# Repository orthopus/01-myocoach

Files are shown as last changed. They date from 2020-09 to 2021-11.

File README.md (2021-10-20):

# 01-myocoach





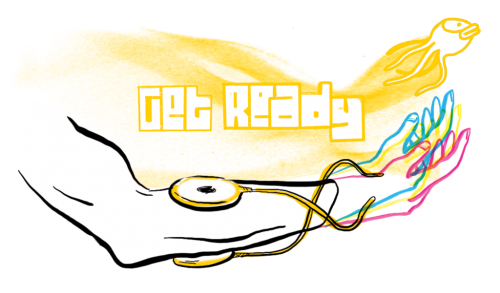
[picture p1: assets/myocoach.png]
myocoach


---

The **MyoCoach** is a device for upper limb amputees who wish to wear a myoelectric prosthesis. It allows you to practice the contraction of the forearm muscles thanks to a video game inspired by Flappy Bird, and to train the control of the future prosthesis.

The MyoCoach can also be used by health professionals, particularly prosthetist (CPO) and occupational therapists, as it allows the myoelectric sensors to be placed correctly and adjusted for optimal use of myoelectric prostheses.

The MyoCoach makes it possible to :

* Measure muscle potential with the help of myoelectric sensors
* Define the optimal sensor position
* Adjusting the sensors using potentiometers
* Exercise in muscle contraction and coordination

The **MyoCoach** is made up of different elements :

* 2 EMG sensors to read the patient's myoelectric signals (EMG)
* 1 box to transfer data to the computer with an Arduino Board
* A holder to hold the sensors on the patient's arm
* A PC to run the UI application for EMG data visualization

> :warning: Today, the MyoCoach uses sensors from the brand Ottobock (Ref 13E202). One day, ORTHOPUS will propose one, but not at the price of 1000€ !
> 

## Warning notice before starting

The versions of our solutions reproduced in Do It Yourself do not have the CE marking. It can only be apply to solutions developed and sold by ORTHOPUS which follow the regulations in force.
ORTHOPUS cannot guarantee the “quality” of solutions replicated by third parties thanks to documentation shared on github.

## D.I.Y Level

:star: :star:

**Required devices** : to make your own Myo coach, we will need a 3D printer and some basics electronics tools like a soldering iron + soldering accessories (you will find a detailed list of equipment in the [user manual](./docs/user-manual.md).

## How to make your own

We give more details about how to get the best experiences with the **Myo Coach** in the [user manual](./docs/user-manual.md).

You can design the MyoCoach for less than **30€**. More details in the [COSTS](COSTS.md) file.

Follow this steps to make your own **Myo Coach**

**:one: Download the src**

Download the [latest release](https://github.com/orthopus/01-myocoach/releases/latest)

or clone the **01-myocoach** repository

```bash
$ git clone https://github.com/orthopus/0102-myocoach-diy.git
```

**:two: Make the box**

Follow the [manufacturing manual](./docs/manufacturing-manual.md)

**:three: Flash the Arduino Board**

Follow the [firmware programming manual](./docs/firmware-programming-manual.md)

**:four: Install the Application server on a Raspberry Pi board**

Follow the [App server programming manual](./docs/server-programming-manual.md)

## Contribution
Your contribution to the MyoCoach project is welcome!

* Have you discovered a bug or you have an improvement ideas ?
  * Go to the GitHub [issues](https://github.com/orthopus/01-myocoach/issues) of the project.
* You have time, some Maker skills and you want to help us ?
  * Read the [CONTRIBUTING](CONTRIBUTING.md) file to help us to go to the **Myo Coach v2.0**
  * Read the [CODEOFCONDUCT](CODEOFCONDUCT.md) file to know community standards

## Contact

If you wish to contact us, you can send a message to contact@orthopus.com

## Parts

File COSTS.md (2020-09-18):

# 0113-MyoCoach-DIY :<br>Price Transparency

## Raw Material Price
| Description | Quantity | Unit Price | Price |
| --- | --- | --- | --- |
| Sensor Support (3D print)| 2 | 0.60€ | 1.20€ |
| Box Casing (3D print)| 1 | 2.18€ | 2.18€ |
| Arduino Board Uno | 1 | 20.00€ | 20.00€ |
| female pin header strip | 1 | 1.17€ | 1.17€ |
| male pin header strip | 1 | 1.07€ | 1.07€ |
| Self-tapping screws | 8 | 0.02€ | 0.16€ |
| strap with velcro and buckle | 1 | 0.50€ | 0.50€ |
| set of electronic cables | 1 | 2.68€ | 2.68 € |
| | | **Total**      | **28.96€** |

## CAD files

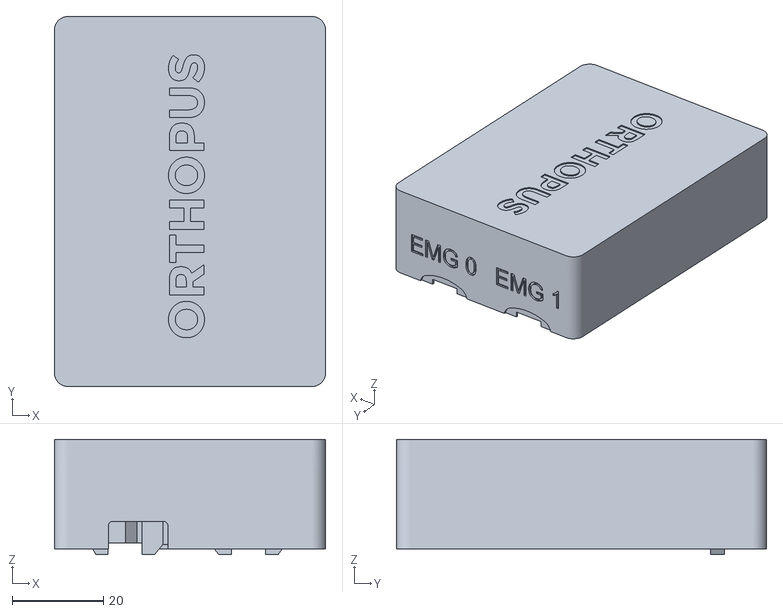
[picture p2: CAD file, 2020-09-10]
src/hardware/casing/Casing Up.stl
59.3 x 80.9 x 25.2

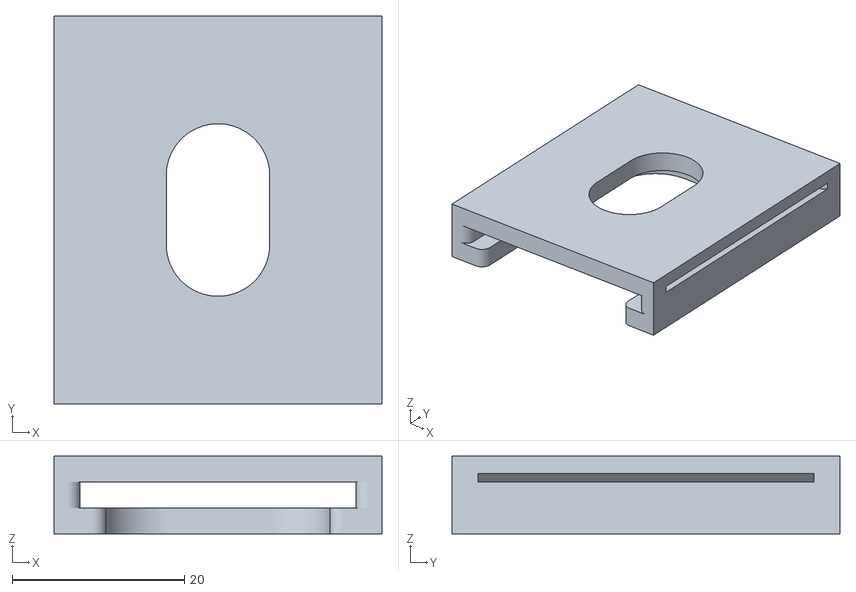
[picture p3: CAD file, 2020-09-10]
src/hardware/casing/Sensor Support 13E202.stl
38.0 x 45.0 x 9.00

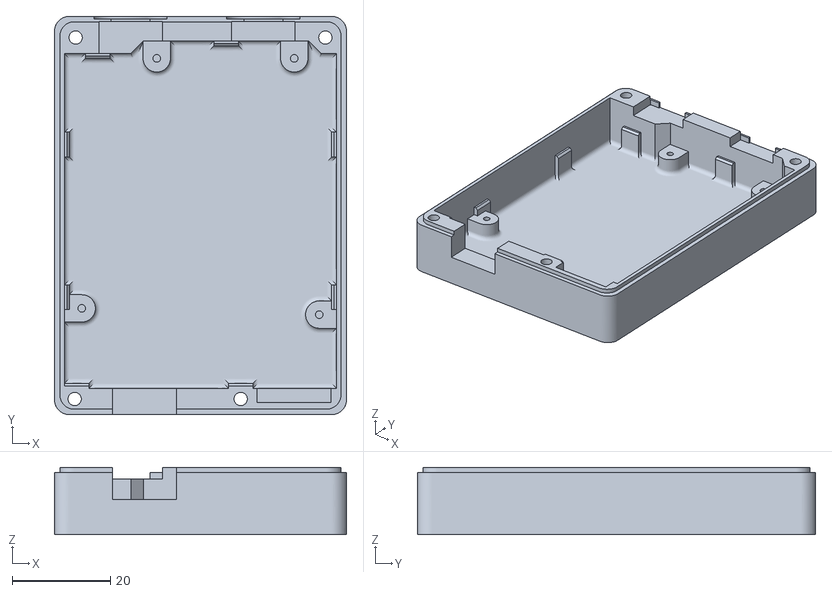
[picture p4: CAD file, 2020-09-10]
src/hardware/casing/Casing Down.stl
59.3 x 80.9 x 13.7

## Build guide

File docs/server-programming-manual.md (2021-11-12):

# 0113-MyoCoach-DIY :<br>Server Programming Guide

myocoach

---

The MyoCoach v2.0 application allows the visualization of raw EMG signals and allows users to train by doing exercises or through video games. As it is a web application with a responsive design, it can be accessed using a web browser installed on a desktop workstation or on a mobile device such as a smartphone or a tablet.  

The MyoCoach v2.0 application has been created using the following technologies :
* Back-end development : Python Flask, SQLite, Socket-IO
* Front-end development : TypeScript, React, Material-UI
* Games development : Godot Engine

The original environment board chosen to host the application is a Raspberry Pi 3 model B+ but the installation process remains identical with later versions of Raspberry Pi boards and can probably be adapted for other development boards or desktop workstations running under a GNU/Linux OS.

## OS setup

Download a Raspberry Pi OS Lite image available at the following address from a workstation : https://www.raspberrypi.org/software/operating-systems/#raspberry-pi-os-32-bit

Unzip the downloaded archive to get the image file (.img file extension).

From a terminal, go to the directory where the .img file is then connect a MicroSD card on the workstation (16Gb A1 minimum recommended). The MicroSD card has to be unmounted if it has been mounted automatically.

Then run the following command :

Note : Replace _2021-05-07-raspios-buster-armhf-lite_ by the actual .img file name.

```bash
~> sudo dd bs=1m if=2021-05-07-raspios-buster-armhf-lite.img of=/dev/rdisk2
```

Eject the MicroSD card from the workstation SD slot then insert it in the Raspberry Pi MicroSD slot. Connect a screen, a keyboard and an ethernet cable then power on the Raspberry Pi board. Wait for the system to be ready.

Once the system started, authenticate on the terminal with "pi" user (password: raspberry).

## SSH access

On the Raspberry Pi, enable ssh access allow remote connection from other workstation. Run the following command :

```bash
pi@raspberrypi:~ $ sudo raspi-config
```

Select the following option on the user interface : _3 Interface Options_, _P2 SSH_ then select _Yes_. Finally, select _Finish_ to save configuration and get back to the command prompt.

## Keyboard layout

It may be necessary to configure the type of keyboard used. Run the following command :

```bash
pi@raspberrypi:~ $ sudo raspi-config
```

Select the following option on the user interface : _5 Localisation Options_, _L3 Keyboard_ then follow the instructions to configure the keyboard (for example : Logitech, French-French (legacy, alt.), The default for the keyboard layout, No compose key). Finally, select _Finish_ to save configuration and back to the command prompt.

## Pi password

To change the default password, run the following command :

```bash
pi@raspberrypi:~ $ passwd
```

Then type the current password, the new password and finally confirm.

## Installing system packages

To install software from the Internet it is necessary to wire-up the Raspberry Pi to a router using the Ethernet interface. To do so plug an RJ45 cable on the Ethernet port of the board and connect-it to a router that has a connection to the Internet.

Before installing new components, it may be necessary to get the up-to-date packages list :

```bash
pi@raspberrypi:~ $ sudo apt udpate
```

As well as the packages installed by default :

```bash
pi@raspberrypi:~ $ sudo apt upgrade
```

The MyoCoach setup needs several packages to work properly : Pip3, VirtualEnv, Flask, NodeJs, SQLite.

First add nodesource apt repository in order to be able to get the nodejs packages :

```bash
pi@raspberrypi:~ $ curl -sL https://deb.nodesource.com/setup_16.x | sudo bash -
```

Then install the packages :

```bash
pi@raspberrypi:~ $ sudo apt install nodejs git python3-pip python3-flask sqlite3 virtualenv
```

## Application setup

### Get the application code

To get the latest version of the application source code, keep the board connected to the Internet using the Ethernet port and run the following commands :

```bash
pi@raspberrypi:~ $ git clone https://github.com/orthopus/01-myocoach.git
```

### Fetch application dependencies

On the Raspberry Pi, go to the MyoCoach webapp directory :

```bash
pi@raspberrypi:~ $ cd 01-myocoach/src/software/webapp/
```

To get the Python packages, run the following command :

```bash
pi@raspberrypi:~/01-myocoach/src/software/webapp $ sudo pip3 install -r requirements.txt
```

Run the following command to get the nodejs dependencies :

```bash
pi@raspberrypi:~/01-myocoach/src/software/webapp $ npm install
```

### Environment variables and compilation

Create a copy of the _.env.example_ file named _.env_ :

```bash
pi@raspberrypi:~/01-myocoach/src/software/webapp $ cp .env.example .env
```

Then check its content and adapt it if necessary using a text editor :

```bash
pi@raspberrypi:~/01-myocoach/src/software/webapp $ nano .env
```

.env
```bash
NODE_ENV=production
ENDPOINT=http://app.myocoach.lan
```

The run the Webpack compilation with the following command :

```bash
pi@raspberrypi:~/01-myocoach/src/software/webapp $ npx webpack --config webpack.prod.js
```

## Networking

### Hostname

In objective to change the MyoCoach hostname (currently raspberrypi), open the system settings interface with the following commands :

```bash
pi@raspberrypi:~ $ sudo raspi-config
```

On the system settings interface, select _1 System Options_, _S4 Hostname_ then _OK_. Type the new name _"myocoach"_. Select _Finish_ to save the configuration. Finally, select _Yes_ to reboot the system for the changes take effect.

The hostname of the _hosts_ file has to be refreshed to save the new hostname.

```bash
pi@myocoach:~ $ less /etc/hosts
```

hosts
```bash
127.0.0.1       localhost
::1             localhost ip6-localhost ip6-loopback
ff02::1         ip6-allnodes
ff02::2         ip6-allrouters

127.0.1.1       myocoach
```

### Avahi configuration

Open the avahi configuration file in order to make MyoCoach get the _"myocoach.lan"_ name on the network :

```bash
pi@myocoach:~ $ sudo nano /etc/avahi/avahi-daemon.conf
```

avahi-daemon.conf
```bash
...
[server]
host-name=myocoach
domain-name=lan
...
```

Restart the service for the changes to take effect with the following commands :

```bash
pi@myocoach:~ $ sudo systemctl reload avahi-daemon
pi@myocoach:~ $ sudo systemctl restart avahi-daemon
```

### Access Point - RaspAP

To enable wireless on the Raspberry Pi use the following command :

```bash
pi@myocoach:~ $ sudo rfkill unblock wlan
```

```bash
pi@myocoach:~ $ curl -sL https://install.raspap.com | bash
```

Then follow the instructions.

Once the Raspberry Pi rebooted, connect to the network raspap-webui (psk: ChangeMe) with the workstation. Go to the access point management interface from the workstation with a web browser at the following address _10.3.141.1_. Authenticate to the interface with the "admin" username (password: secret) then go to the Authentication section to change the password.

### Captive portal

The captive portal is managed by the Nodogsplash application.

```bash
pi@myocoach:~ $ sudo apt-get install libmicrohttpd-dev
```

```bash
pi@myocoach:~ $ sudo mkdir /srv/nodogsplash
pi@myocoach:~ $ sudo chown pi /srv/nodogsplash
pi@myocoach:~ $ sudo chgrp pi /srv/nodogsplash
pi@myocoach:~ $ git clone https://github.com/nodogsplash/nodogsplash.git /srv/nodogsplash
```

To compile Nodogsplash, run the following commands :

```bash
pi@myocoach:~ $ cd /srv/nodogsplash
pi@myocoach:~ $ make
pi@myocoach:~ $ sudo make install
```

Open the configuration file nodogsplash.conf :

```bash
pi@myocoach:~ $ sudo nano /etc/nodogsplash/nodogsplash.conf
```

Change the following lines :

```bash
GatewayInterface wlan0
GatewayAddress 10.3.141.1
RedirectURL http://10.3.141.1:2050/redirect.html
```

In the FirewallRuleSet users-to-router object, add the following line :

```bash
FirewallRule allow tcp port 5000
```

Save and close the file.

Remove nodogsplash default captive portal html files :

```bash
pi@myocoach:~ $ sudo rm -rf /etc/nodogsplash/htdocs
```

Then create a link to myocoach captive portal html files :

```bash
pi@myocoach:~ $ sudo ln -s /home/pi/01-myocoach/src/software/captiveportal /etc/nodogsplash/htdocs
```

Open the configuration file dnsmasq.conf :

```bash
pi@myocoach:~ $ sudo nano /etc/dnsmasq.conf
```

Add or change the following line :

```bash
address=/#/10.3.141.1
```

Save and close the file. 

Copy the nodogsplash.service file then enable start at boot :

```bash
pi@myocoach:~ $ sudo cp /srv/nodogsplash/debian/nodogsplash.service /lib/systemd/system/
pi@myocoach:~ $ sudo systemctl enable nodogsplash.service
```

Enable start at boot :

```bash
pi@myocoach:~ $ sudo systemctl enable dnsmasq.service
```

Finally, reboot the system to save the changes.

### Lighttpd configuration

In objective to access the MyoCoach web interface and the RaspAP web interface as well, Lighttpd has to be configured.

First, the RaspAP web interface must have restricted access to the _raspap.myocoach.lan_ subdomain name.

```bash
pi@myocoach:~ $ sudo nano /etc/lighttpd/conf-available/50-raspap-router.conf
```

50-raspap-router.conf
```bash
server.modules += ("mod_rewrite")

$HTTP["host"] == "raspap.myocoach.lan" {
  $HTTP["url"] =~ "^/(?!(dist|app|ajax|config)).*" {
    url.rewrite-once = ( "^/(.*?)(\?.+)?$"=>"/index.php/$1$2" )
    server.error-handler-404 = "/index.php"
  }
}
```

Next, create a new file to declare the virtual host _app.myocoach.lan_.

```bash
pi@myocoach:~ $ sudo nano /etc/lighttpd/conf-available/40-myocoach.conf
```

40-myocoach.conf
```bash
server.modules += ( "mod_proxy" )

# proxy myocoach
$HTTP["host"] == "app.myocoach.lan" {
  proxy.debug = 1
  proxy.server = ( "" => ( ( "host" => "10.3.141.1", "port" => "5000" ) ) )
  proxy.header = ( "upgrade" => "enabled" )
}
```

Then, create a link to activate this new host.

```bash
pi@myocoach:~ $ cd /etc/lighttpd/conf-enabled/
pi@myocoach:~ $ sudo ln -s ../conf-available/40-myocoach.conf
```

At last, reboot the service for the changes to take effect.

```bash
pi@myocoach:~ $ sudo systemctl reload lighttpd
pi@myocoach:~ $ sudo systemctl restart lighttpd
```

## MyoCoach service

Create a link named myocoach in the /srv directory to the webapp directory :

```bash
pi@myocoach:~ $ sudo ln -s /home/pi/01-myocoach/src/software/webapp /srv/myocoach
```

Create a link named ledbutton in the /srv directory to the ledbutton directory :

```bash
pi@myocoach:~ $ sudo ln -s /home/pi/01-myocoach/src/software/ledbutton /srv/ledbutton
```

Create the MyoCoach systemd service :

```bash
pi@myocoach:~ $ cd /lib/systemd/system
pi@myocoach:/lib/systemd/system $ sudo nano myocoach.service
```

myocoach.service
```bash
[Unit]
Description= Controls myocoach webapp service
Requires= lighttpd.service
After= lighttpd.service

[Install]
WantedBy= multi-user.target

[Service]
Type= simple
User= root
WorkingDirectory= /srv/myocoach/app
ExecStart= /bin/python3 ./app.py
ExecStartPost= /bin/bash /srv/ledbutton/set_led_color.sh 0 0 255 0
ExecStop= /bin/kill -2 $MAINPID
ExecStopPost= /bin/bash /srv/ledbutton/set_led_color.sh 255 255 255 0
```

To start the service run the following command :

```bash
pi@myocoah:~ $ sudo systemctl start myocoach.service
```

To enable the service at system boot run the following command :

```bash
pi@myocoah:~ $ sudo systemctl enable myocoach.service
```

The MyoCoach web interface is now reachable at the following address :
_http://app.myocoach.lan_

And the RaspAP web interface is now reachable at the following address :
_http://raspap.myocoach.lan_

## LED Power Button Configuration (optional)

Optionally the MyoCoach can be equipped with a LED Power Button. It allows users to have information about the system state and proceed to a more graceful Power-OFF of the board (ie. cleaner than unplugging the power cable).

Create systemd services :

```bash
pi@myocoach:~ $ cd /lib/systemd/system
pi@myocoach:/lib/systemd/system $ sudo nano enlight_led.service
```

enlight_led.service
```bash
[Unit]
Description= Launch enlight_led.service

[Install]
WantedBy=multi-user.target

[Service]
Type= simple
User= pi
WorkingDirectory= /srv/ledbutton
ExecStart= /bin/bash ./enlight_led.sh
```

```bash
pi@myocoach:/lib/systemd/system $ sudo nano check_color_changed.service
```

check_color_changed.service
```bash
[Unit]
Description= Restarts enlight_led.service
Requires=basic.target
After=basic.target

[Install]
WantedBy=multi-user.target

[Service]
Type= oneshot
ExecStart= /usr/bin/systemctl restart enlight_led.service
```

```bash
pi@myocoach:/lib/systemd/system $ sudo nano check_color_changed.path
```

check_color_changed.path
```bash
[Unit]
Wants= check_color_changed.service

[Path]
PathChanged= /srv/ledbutton/led_color.txt

[Install]
WantedBy=basic.target
```

```bash
pi@myocoach:/lib/systemd/system $ sudo nano set_led_color_on_system_startup.service
```

set_led_color_on_system_startup.service
```bash
[Unit]
Description= Set led color on system startup
Requires= basic.target
After=basic.target

[Install]
WantedBy=multi-user.target

[Service]
Type= oneshot
WorkingDirectory= /srv/ledbutton
ExecStart= /bin/bash ./set_led_color.sh 255 255 255 0
```

Enable start at boot :

```bash
pi@myocoach:~ $ sudo systemctl enable enlight_led.service
pi@myocoach:~ $ sudo systemctl enable check_color_changed.service
pi@myocoach:~ $ sudo systemctl enable check_color_changed.path
pi@myocoach:~ $ sudo systemctl enable set_led_color_on_system_startup.service
```

Open the configuration file config.txt :

```bash
pi@myocoach:~ $ sudo nano /boot/config.txt
```

Add the following line :

```bash
dtoverlay=gpio-shutdown
```

Save and close the file. Finally, reboot the system to apply the changes.
```bash
pi@myocoach:~ $ sudo reboot
```

## Add new Games

The MyoCoach application has been designed to host video games developed using the Godot environment and that are adapted to use EMG signals as inputs.

Further information about game development with Godot can be found on Godot Engine website : _https://godotengine.org/_

To integrate new games in the MyoCoach environment and make them available from the web application, here are some guide-lines :

As there are only two EMG signals, and thus two possible inputs, the gameplay has to be kept simple. These EMG signals are mapped to InputEventMouseMotion in order to keep the "analog" values of signals. Depending on the game design, the value of EMG signals can be used as proportional inputs directly or to trigger events when they exceed a defined threshold.

A folder has to be created under the public/games/ directory for each hosted game. As an exemple to add "Squash" game, run the following command :

```bash
pi@myocoach:~ $ cd /srv/myocoach/public/games/ 
pi@myocoach:/srv/myocoach/public/games $ mkdir squash
```

From the Godot development environment, the games must be exported using an HTML5 template. Once exported, if the name of the export chosen is _game.html_, then get the files _game.pck_ and _game.wasm_ copy them in the freshly created folder.

```bash
pi@myocoach:/srv/myocoach/public/games $ ls squash/
game.pck  game.wasm
```

For each game a description with its metadata must be indicated in the _gamelist.json_ file.

Open the _gamelist.json_ with a text editor to add the necessary info :

```bash
pi@myocoach:/srv/myocoach/public/games $ nano gamelist.json
```

As an example, for a MyoCoach setup with the games "FlappyPoulpy" and "Squash" installed, _gamelist.json_ might contain the following lines :

gamelist.json
```json
[
  {
    "name": "FlappyPoulpy",
    "url": "/flappypoulpy",
    "path": "flappypoulpy",
    "width": 340,
    "height": 256,
    "fileSizes": {
      "/public/games/flappypoulpy/game.pck": 1191008,
      "/public/games/flappypoulpy/game.wasm": 18131449
    }
  },
  {
    "name": "Squash",
    "url": "/squash",
    "path": "squash",
    "width": 640,
    "height": 400,
    "fileSizes": {
      "/public/games/squash/game.pck": 16352,
      "/public/games/squash/game.wasm": 18149419
    }
  }
]
```

Once the information filled in, save and close the file.

The file size information for _game.pck_ and _game.wasm_ can be found looking in the _game.html_ file that has been generated during the export. It is important to fill in this information in order to make the game loader work properly.

The screen dimensions (width and height in number of pixels) are the default game screen dimensions that can be found in Godot development environment. It is important to fill in this information in order to make the MyoCoach web application keep the game's screen aspect ratio whatever the device screen size is.

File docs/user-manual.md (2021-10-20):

# 0113-MyoCoach-DIY :<br>User Manual

myocoach

---

The MyoCoach system is intended for health care professional and users of upper limb prostheses. Its features allow to :

* Measure muscle potential using myoelectric sensors
* Defining the optimum electrode position
* Adjusting the myoelectric electrodes
* Exercise in muscle contraction and coordination

## Prerequisites and features
 * 1 Personal Computer with a Wi-Fi network interface (or smartphone/tablet) with a web browser
 * 1 MyoCoach box :one:
 * 1 USB cable (Arduino) :two:
 * 2 Ottobock electrodes (Ref 13E202) :three:
 * 2 Electrode cables :four:
 * 2 Electrode holders :five:
 * 1 Velcro strap :six:
 * 1 Flat screwdriver :seven:
 * 1 pencil (watercolour type)

_!TODO: IMAGE UPDATE REQUIRED!_

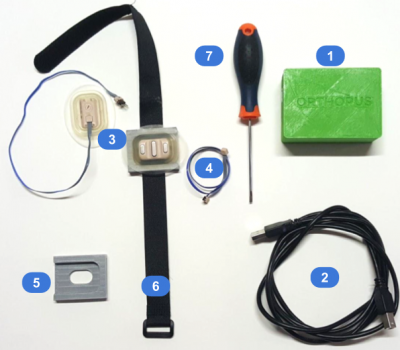
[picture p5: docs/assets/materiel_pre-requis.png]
materiel_pre-requis


The application and the MyoCoach box allow the user to test his ability to control a myoelectric prosthesis. These tests are carried out on a computer and are close to real-life conditions.

The interactive exercises and the video game integrated into the application allows fun muscle training. In addition, it accelerates the learning of the dissociation of the different muscle groups.

Two 13E202 electrodes connected to the MyoCoach box receive the user's myoelectric muscle signals. These signals are then sent to the connected devices to be displayed in a web browser.

The MyoCoach is switched on by plugging in the box power supply to a USB charger or the USB port of a PC. Then the user must connect his device (PC, smartphone or tablet) to the MyoCoach Wi-Fi network.

To switch off the MyoCoach, go to the "Settings" section of the web application and hit the "Shutdown" button. Or if the MyoCoach is equipped with an LED power button (optional) simply push-it.

## Safety instructions
> :warning: Make sure that no solid or liquid particles can get inside the housing.

> :warning: Do not expose the unit to intensive fumes or dust, mechanical vibrations, shocks or excessive temperatures.

> :warning: Avoid using the MyoCoach near sources of major electrical and magnetic interference (transformers or transmitters for example).

> :warning: Respect pauses during use, as muscular fatigue produces irregular results which can lead to the electrodes being adjusted too sensitively.

> :warning: Make sure that the contact surface of the electrodes is applied to healthy skin. If significant malfunctions are detected, the position of the electrodes should be checked and modified if necessary. Refer to the paragraph on electrode placement for more information.

> :warning: The use of a battery charger on the laptop will in most cases interfere with the operation of the electrodes, i.e. the value without any electrode activity is not zero. It is recommended to disconnect the mains power supply during myoelectric data recording and to run the laptop on battery power.

## Electrodes placement protocol
The primary function of the MyoCoach is to optimise electrode placement and find the right gain setting.

For this protocol, we use Ottobock electrodes (Ref 13E202).

This protocol is the result of a scientific publication from the University of Salford (UK).

> :bulb: Chadwell Alix, Kenney Laurence, Thies Sibylle, Galpin Adam, Head John (2016) The Reality of Myoelectric Prostheses: Understanding What Makes These Devices Difficult for Some Users to Control [url](https://www.frontiersin.org/articles/10.3389/fnbot.2016.00007/full)

This test protocol allows the placement of two electrodes which are useful for the use of a myoelectric prosthesis. We use two groups of wrist muscles to control the prosthesis:

* the **flexor muscles** of the wrist to **close the hand** of the prosthesis (1)
* the **extensor muscles** of the wrist to **open the hand** of the prosthesis (2)

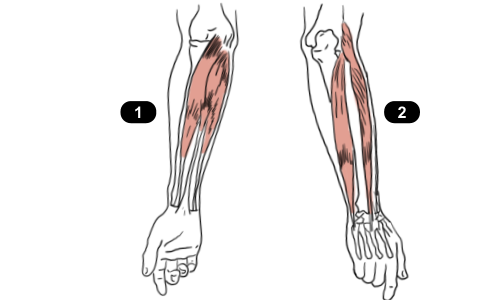
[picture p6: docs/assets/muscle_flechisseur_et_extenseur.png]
muscle_flechisseur_et_extenseur


* :one: - Equip an electrode with a pin header strip to make an adapter with the MyoCoach connector system (see the electrode connector section in the [manufacturing-manual](./manufacturing-manual.md)).

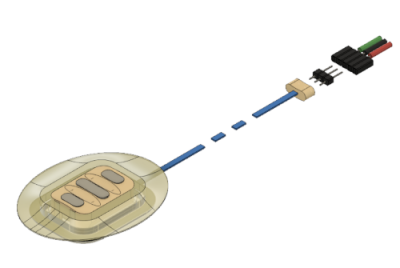
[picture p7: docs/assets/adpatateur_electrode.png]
adpatateur_electrode


* :two: - Adjust the electrode gain to a medium level between 3-4

To access the gain adjustment potentiometer of the Ottobock 13E202 sensor, it is not necessary to remove the sensor from the armband! Simply move it as shown below.

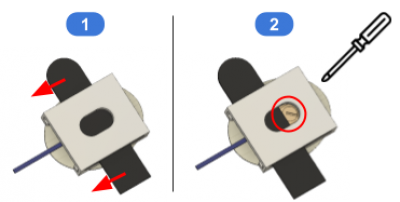
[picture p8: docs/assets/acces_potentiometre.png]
acces_potentiometre


* :three: - Connect this electrode to the EMG 0 connector of the MyoCoach housing.

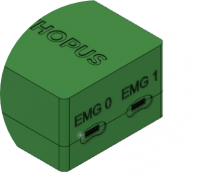
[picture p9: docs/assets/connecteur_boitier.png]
connecteur_boitier


* :four: - Connect the MyoCoach box to the computer using the USB cable supplied with the Arduino card.

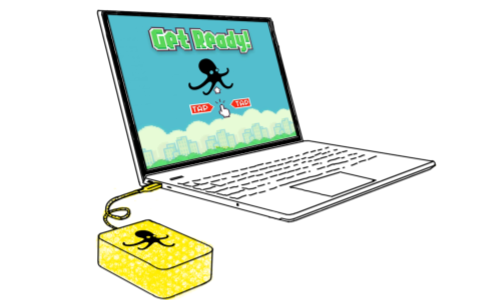
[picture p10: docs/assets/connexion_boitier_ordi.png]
connexion_boitier_ordi


* :five: - Launch the MyoCoach application on the computer, connect the application to the Arduino card and choose the Signal Widget.
* :six: - Hold the electrode on the user's muscle.

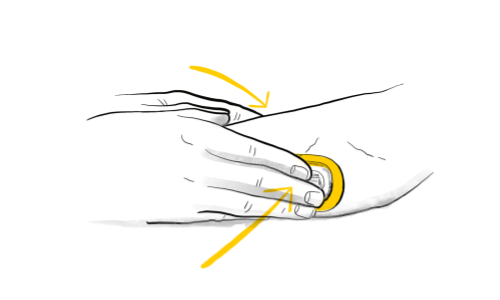
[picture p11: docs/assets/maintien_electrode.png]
maintien_electrode


An EMG electrode must be placed along and in the middle of the muscle fibre.

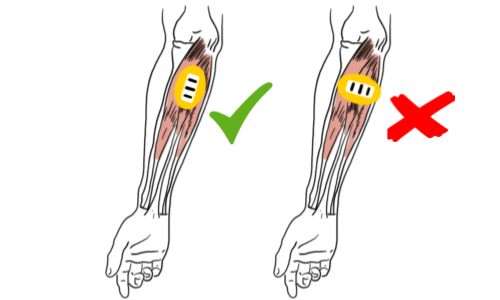
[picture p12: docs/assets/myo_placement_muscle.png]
myo_placement_muscle


* :seven: - Ask the user to repeatedly and regularly contract the muscle concerned by the electrode at a comfortable level, without too much muscle intensity. Note the level of the signal obtained.

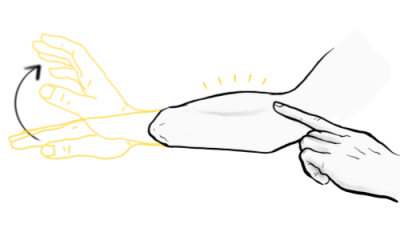
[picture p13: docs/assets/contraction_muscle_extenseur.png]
contraction_muscle_extenseur


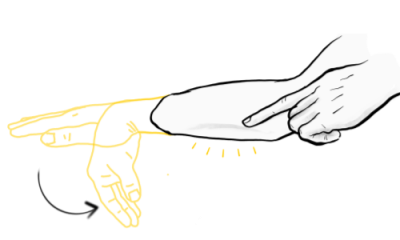
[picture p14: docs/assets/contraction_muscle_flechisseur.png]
contraction_muscle_flechisseur


* :eight: - Then move the electrode in the 4 directions (up, down, left and right) from the starting position. The movement should be about half the width of the electrode (1 cm).

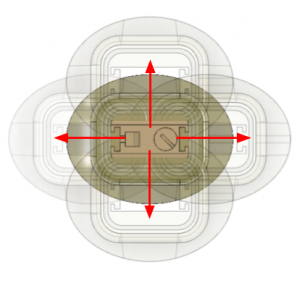
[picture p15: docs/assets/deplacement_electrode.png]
deplacement_electrode


* :nine: - If the signal amplitude is greater at one of the new positions, repeat step :eight:, defining this new position as the starting point.

* :keycap_ten: - The position with the maximum amplitude is then marked on the user's skin with a **pencil**.

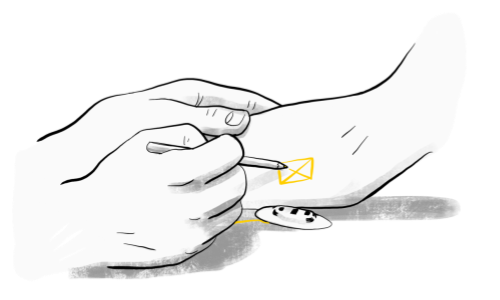
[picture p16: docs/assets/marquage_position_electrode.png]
marquage_position_electrode


* Finally, the gain adjustment is defined so that the user can comfortably reach a signal level between 20 and 80% on the application's Signal Widget.

> :bulb: This protocol must be repeated for the second electrode.

### Connect Electrode to the box

:one: - Assemble the two electrodes on the armband. The armband offers several degrees of freedom to allow the electrodes to be positioned optimally on the user's arm. (See the section ArmBand: Adjustments and positioning in the [manufacturing-manual](./manufacturing-manual.md)).

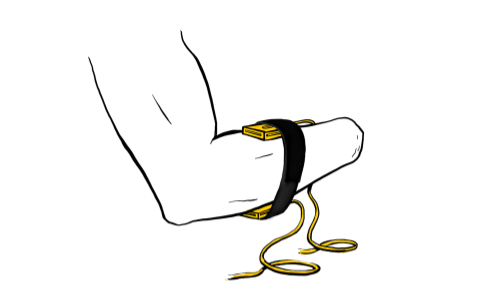
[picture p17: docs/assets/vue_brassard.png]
vue_brassard


:two: - Connect the electrodes to the MyoCoach housing.
* The electrode on the **outside** of the forearm must be connected to the **EMG 0** connector of the housing.
* The electrode placed **inside** the forearm must be connected to the **EMG 1** connector of the housing.

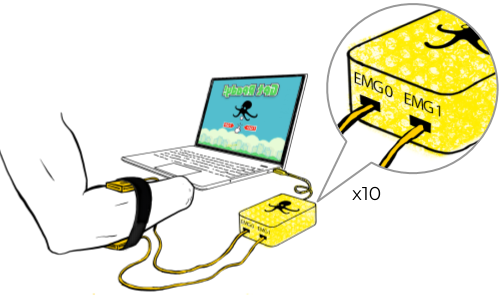
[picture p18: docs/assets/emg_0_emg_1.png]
emg_0_emg_1


Once the electrodes have been connected and the ArmBand adjusted, the user is ready to practice using EMG sensors! :muscle:

## Application overview

The MyoCoach web application is hosted on a Raspberry Pi computer. The Raspberry Pi is set as a Wi-Fi access point and the application can be accessed by connected clients using a web browser.

For full feature support and a good user experience, we recommend to use of one of the following web browsers  :

* Firefox Browser (ver. 93)
* Google Chrome/Chromium (ver. 88)

### Getting started

* :one: - Connect the Raspberry Pi with a USB cable. If equipped, the LED button will light up in white.
* :two: - Wait until the MyoCoach is ready to use. If equipped, the LED button color must change to blue when the system is ready.
* :three: - Connect your client device (PC, phone or tablet) to the MyoCoach network by Wi-Fi. The credentials can be :
   * previously configured with the INSTALL-en document
   * previously configured by Orthopus - SSID = myocoach-01, secret = null (no passphrase)
   * not configured, default value - SSID = raspi-webgui, secret = ChangeMe
* :four: - A captive portal shows up automatically :

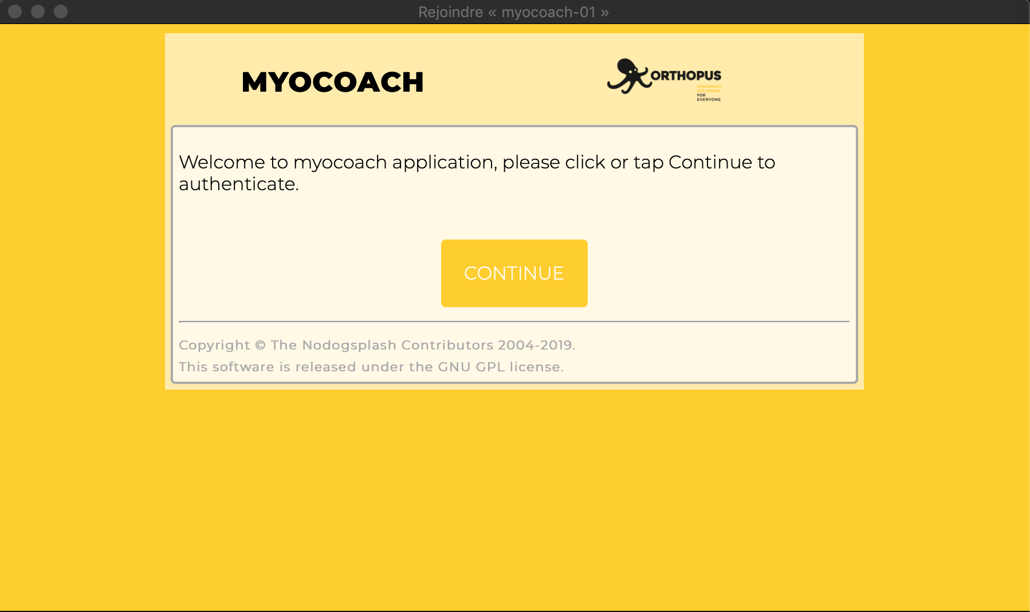
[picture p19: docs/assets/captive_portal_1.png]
captive_portal_1


Click or tap on Continue to authenticate.

* :five: - A new page shows up with the link to access the web application :

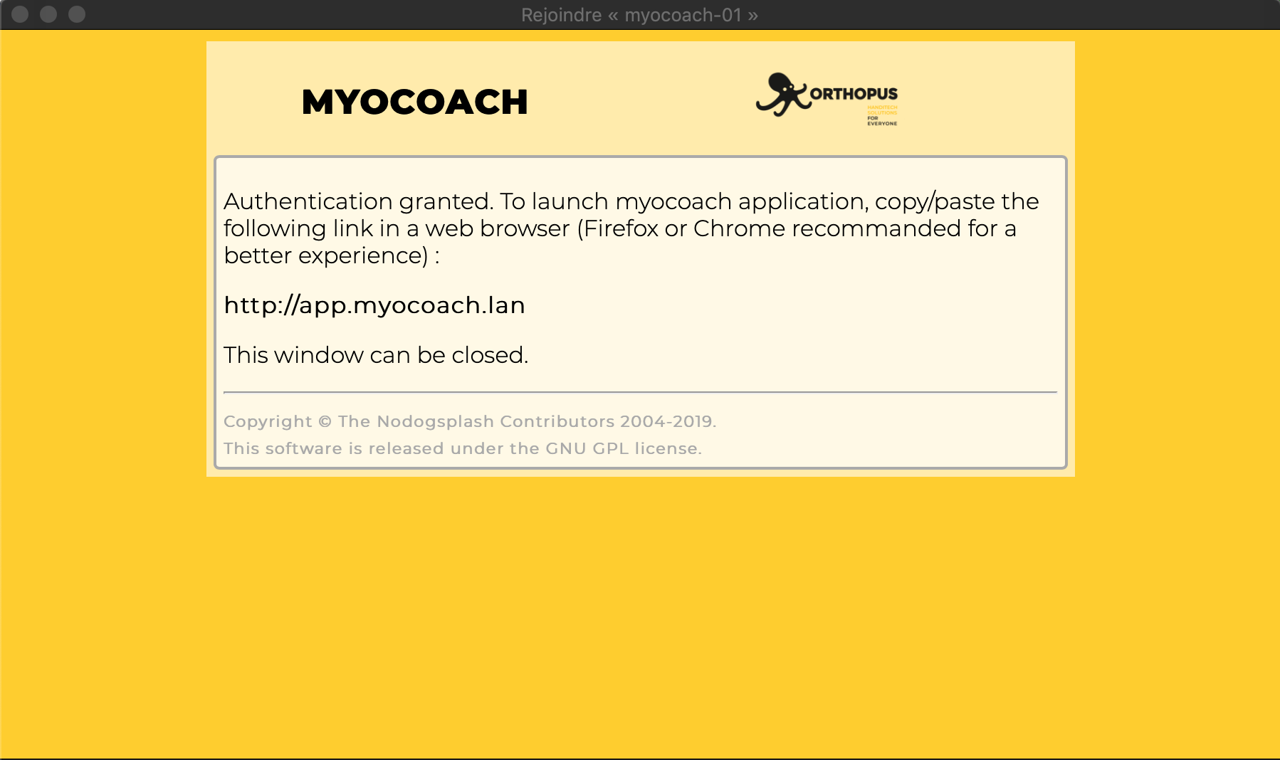
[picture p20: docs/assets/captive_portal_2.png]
captive_portal_2


Copy then paste the link in a web browser. The captive portal window can now be closed.

* :six: - The MyoCoach web application starts with the following section :

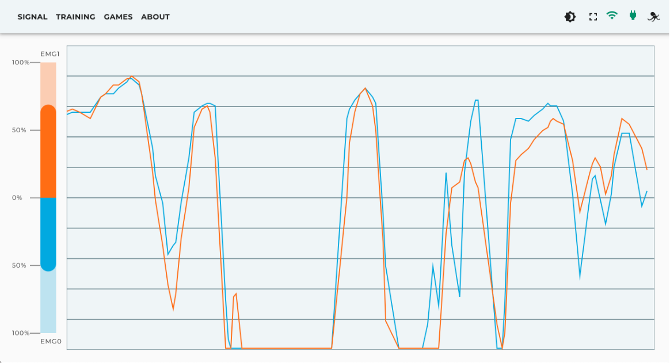
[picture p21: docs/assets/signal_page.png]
signal_page


To use the MyoCoach application on a smartphone or a tablet, we recommend setting the device screen in horizontal (landscape) mode.

* :seven: - The shutdown and restart procedures are explained in the Settings section part. Push on the LED button (if equipped) for a straight shutdown.

### Main app bar
The main app bar allows user to navigate through all sections of the application and watch the system state. Depending on the client device screen width, the app bar can be displayed on the left or at the top of the screen :

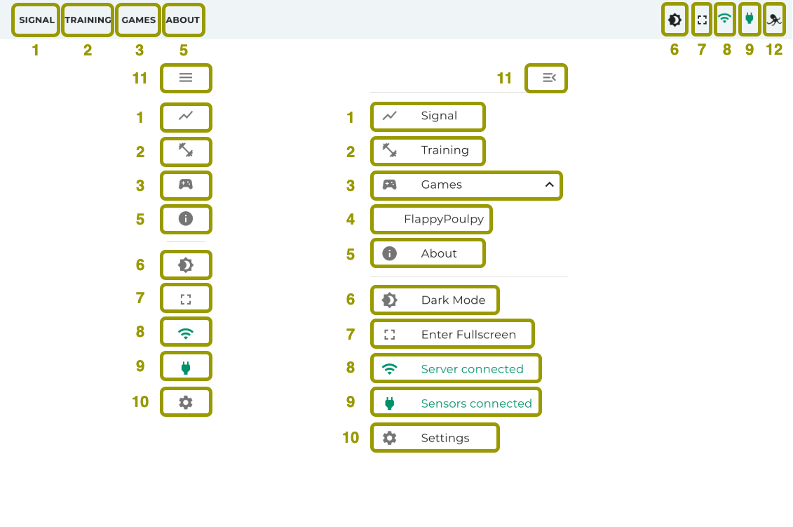
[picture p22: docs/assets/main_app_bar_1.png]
main_app_bar_1


1. Go to Signal section (default section)
2. Go to Training section
3. Extend/reduce games list
4. Go to "FlappyPoulpy" game section
5. Go to About section
6. Enable/disable dark mode (default value depends of the client device OS settings)
7. Enable/disable fullscreen mode (not available on Safari web browser)
8. Server connection state
9. Sensors cardboard connection state
10. Go to Settings section
11. Extend/reduce main app bar
12. Show/hide the application menu

### Dashboard
The dashboard component display the EMG sensors measures :

dashboard

This component is visible on all sections.

### Signal section

The signal section is the application default section and displays EMG sensors measures plots :

signal_page

### Training section

The training section offers several exercises to perform with EMG sensors. The first view invite the user to set up and launch a training session and/or create new custom trails.

#### Training session setup

The training session setup allows user to configure a session before start a training session.

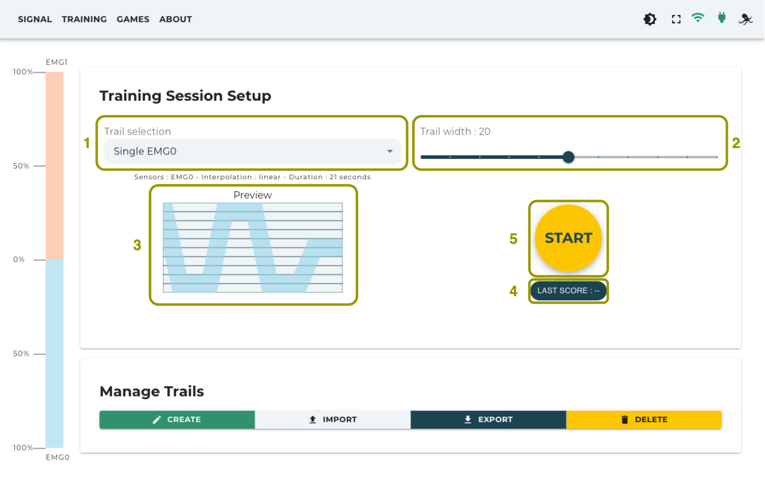
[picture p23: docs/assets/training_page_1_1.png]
training_page_1_1


* :one: - Trail selection list contains all created trails from the manage trails section.
* :two: - Trail width slider sets the trail width from 10 to 30 to adjust the training session difficulty level.
* :three: - A graphical preview of the selected trail.
* :four: - The Last Score chip displays the previous session score.
* :five: - The Start button launches the session.

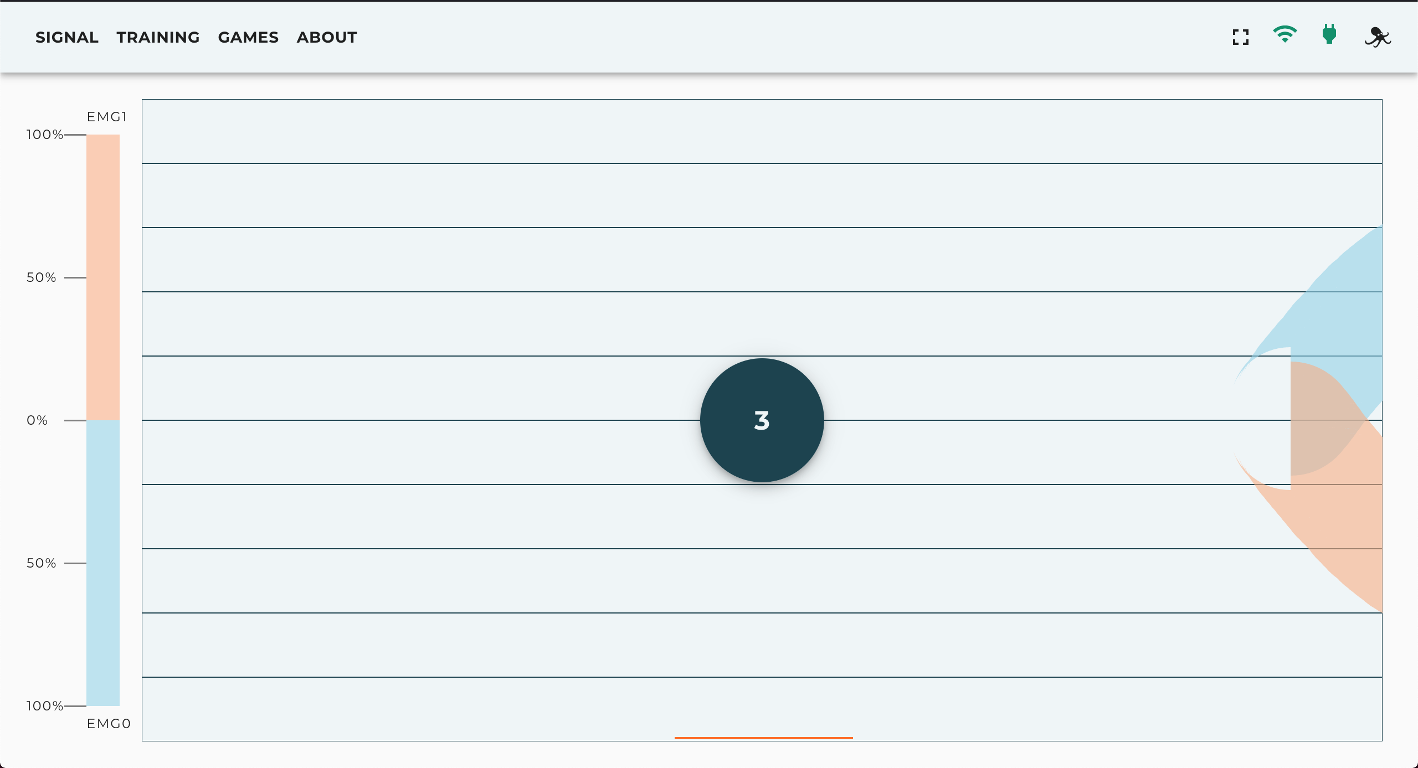
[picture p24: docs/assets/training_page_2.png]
training_page_2


Before the session starts, a centered countdown appears to get ready. The session can be aborted with a click or tap on the countdown to back to the Training Session Setup.

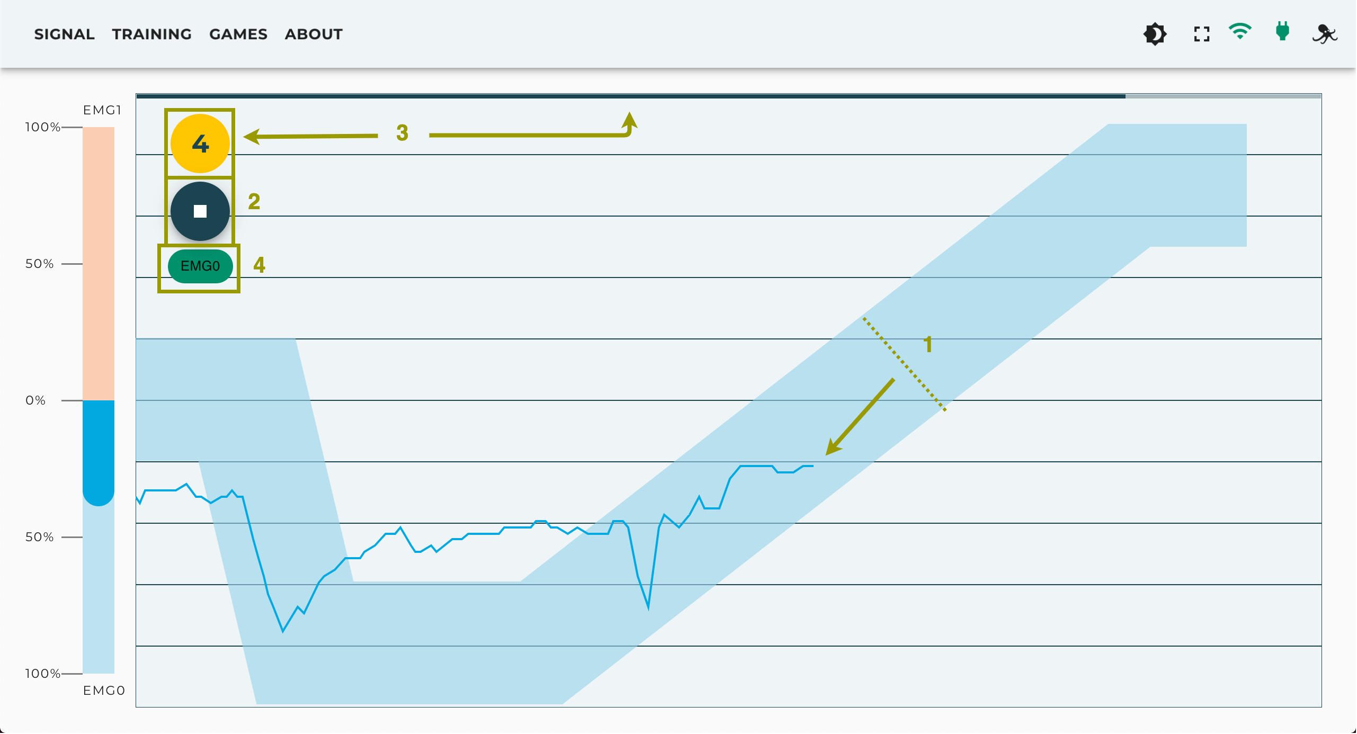
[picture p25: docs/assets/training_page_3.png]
training_page_3


* The purpose of the exercise is to make EMG signal plots remain in the corresponding color path for the time of the session.
* The session can be aborted with a click or tap on the "Stop" button to get back to the Training Session Setup.
* The duration of the session is indicated by the countdown and the progressive bar.
* The color of these chips depends on whether the EMG signal plots are in or out of the path.

#### Manage trails

The manage trails section allows creating, importing, exporting and deleting trails :

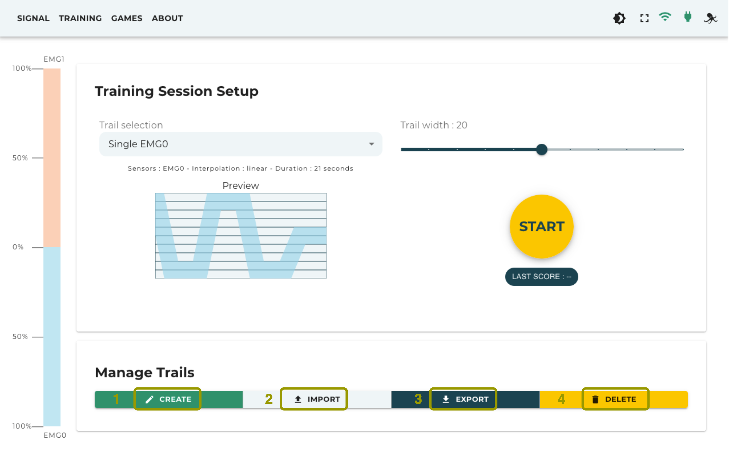
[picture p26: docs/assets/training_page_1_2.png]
training_page_1_2


* Clicking the create button will open up a dialog box to create a new trail with the following specifications :

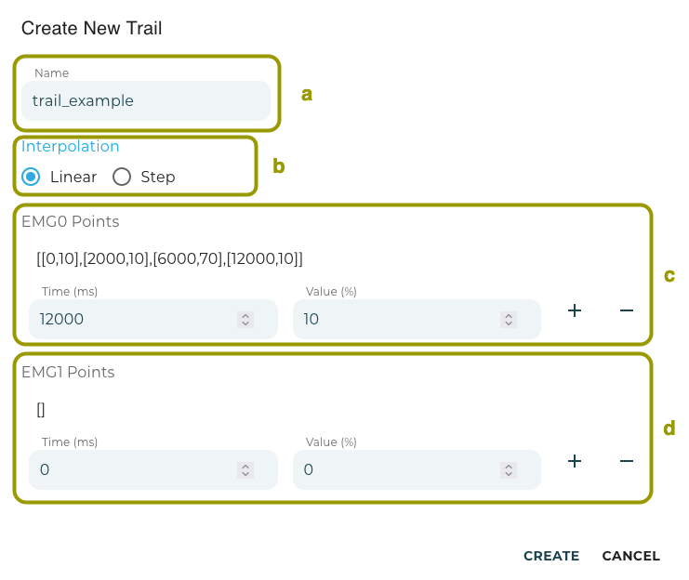
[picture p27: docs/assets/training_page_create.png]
training_page_create


In MyoCoach application, a trail is a set of time/value points.
  * a - The trail name that will appear in the trail selection list and will also be the given file name in case of export.
  * b - The interpolation type defines how two following points will be linked in the trail.
  * c - The EMG0 Points section allows to append the set of time/value points. Use the "Plus" button to append, and the "Minus" to remove the last appended element.
  * d - The EMG1 Points section has the same functionalities as the section above. To use only one sensor, the other set must remain empty

* Clicking the export button will open up a dialog box with the trail list. Clicking the "Export" button will generate then download the selected trail in a .xlm file that can be uploaded to another MyoCoach device (using the import trail feature) :

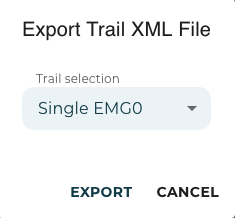
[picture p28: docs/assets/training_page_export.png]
training_page_export


* Clicking the import button will open up a dialog box to upload .xml compatible file. The "Browse..." button allows user to choose the file to import on the client file system and then append it to the trail selection list :

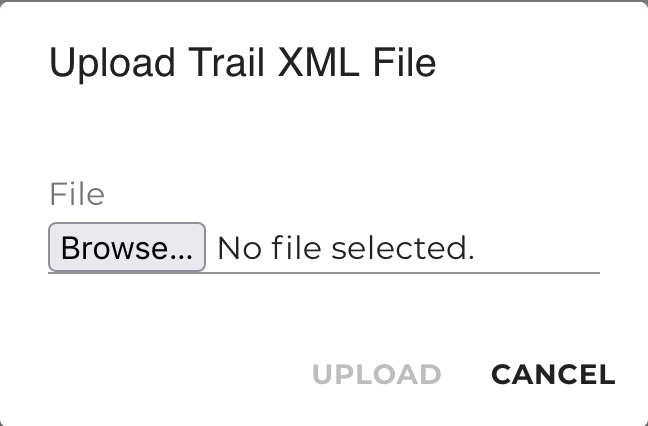
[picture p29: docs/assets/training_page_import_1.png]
training_page_import_1


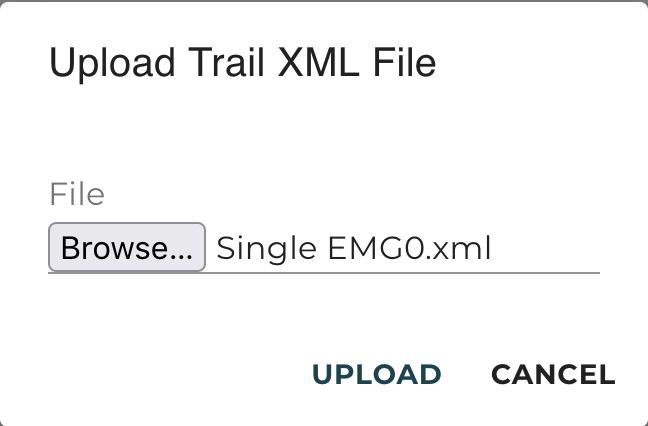
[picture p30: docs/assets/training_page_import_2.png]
training_page_import_2


* Clicking the delete button will open up a dialog box with the trail list. The "Delete" button removes the selected trail :

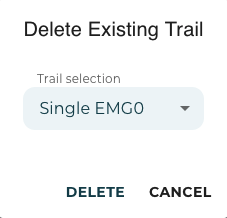
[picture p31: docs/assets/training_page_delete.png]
training_page_delete


### Game section

The games available in MyoCoach are an entertaining alternative to practice EMG sensor control.

By default, one game is available on the MyoCoach : FlappyPoulpy

FlappyPoulpy is a FlappyBird-like game that uses EMG sensors as a controller.

* Once the game has finished loading, the following screen shows up :

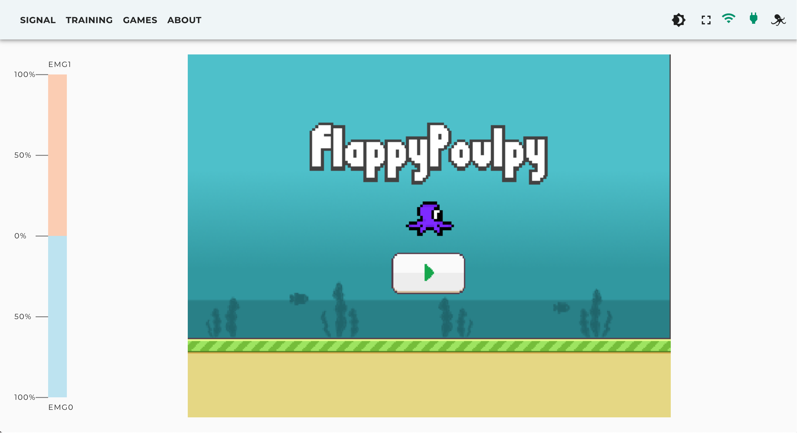
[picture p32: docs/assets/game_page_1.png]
game_page_1


* Click or tap on the "Play" button to continue. Then a view shows up and explains how to use EMG sensors as a controller. Click, tap or exceed the 30% threshold with the EMG1 sensor (visible with the Dashboard component) to start the game :

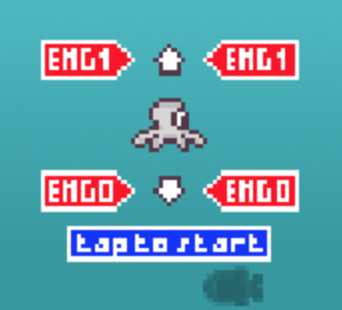
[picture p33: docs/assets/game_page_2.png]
game_page_2


* Once the game started the objective is to go through the "gates" between two column and reach the best score possible. With each gate passed the score and speed of play increase :

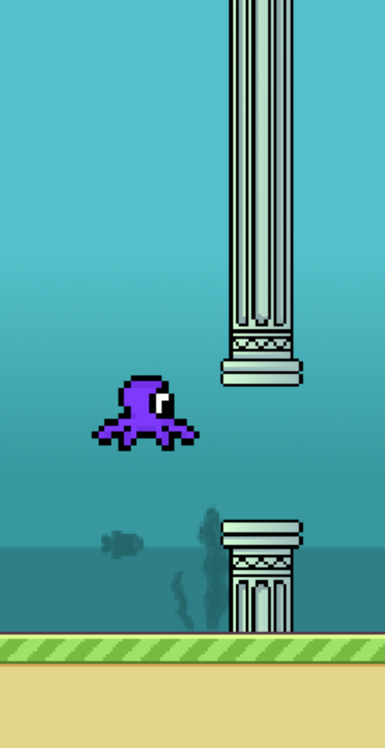
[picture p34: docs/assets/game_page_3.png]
game_page_3


* In case of missing a passage the game over screen shows up displaying the score reached. Click or tap on the "Play" button or exceed the 30% threshold with the EMG1 sensor to start a new game :

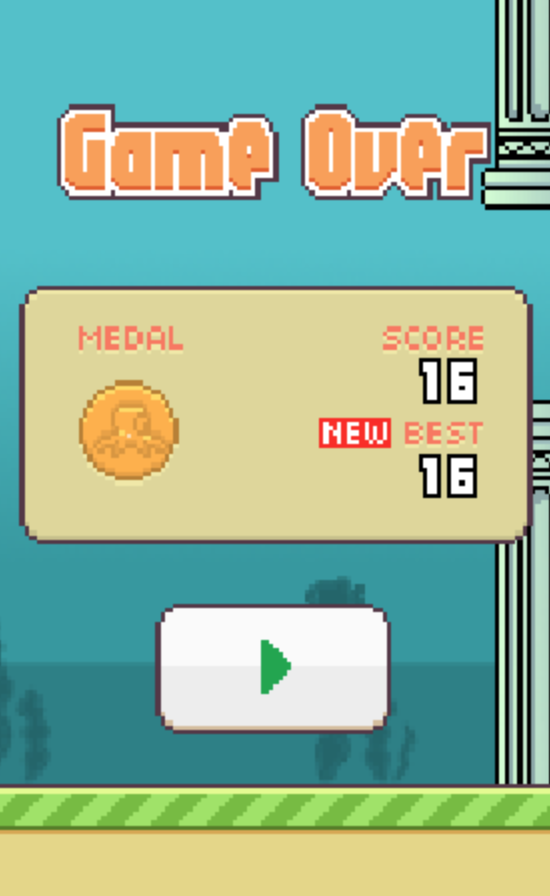
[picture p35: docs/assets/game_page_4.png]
game_page_4


### About section

The about section shows additional information about the MyoCoach project and Orthopus :

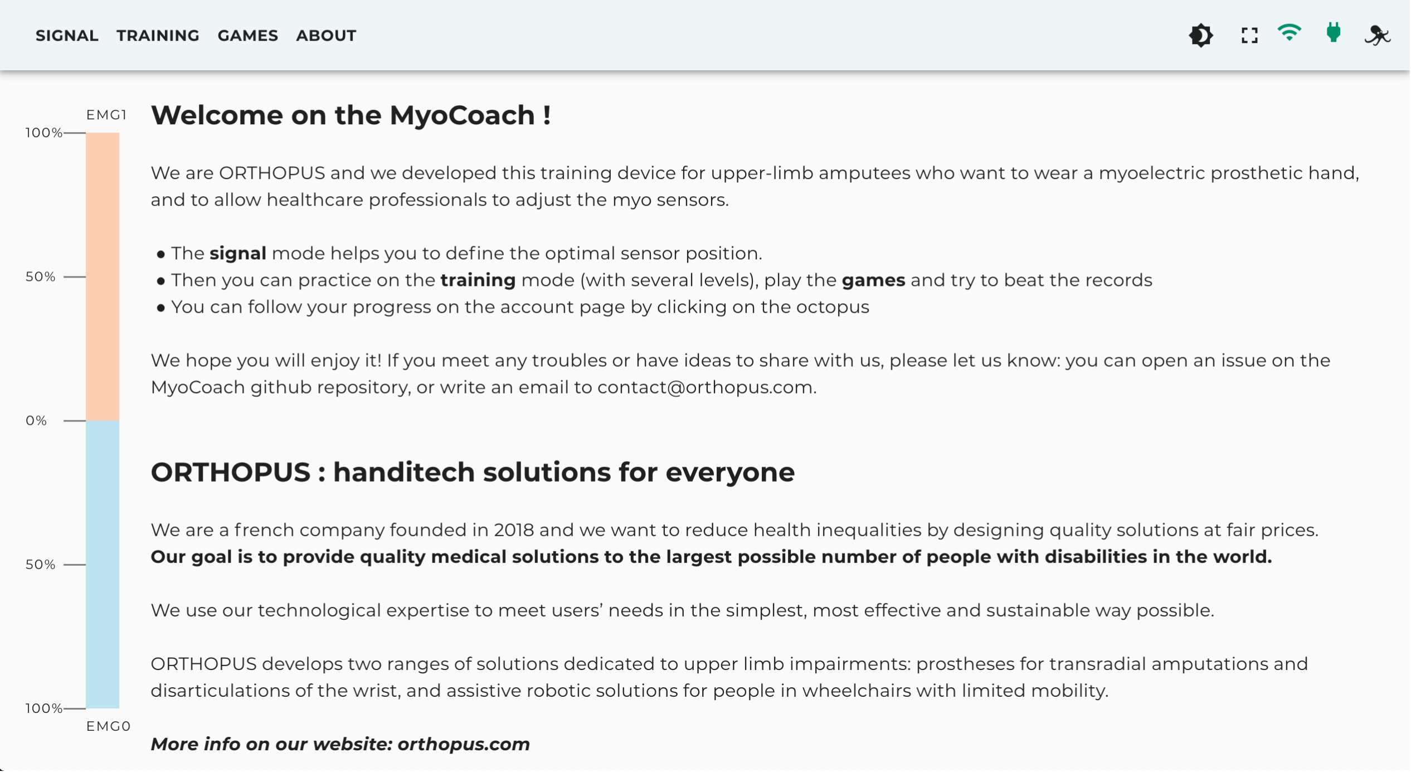
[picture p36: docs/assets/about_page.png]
about_page


### Settings section

The settings section shows the MyoCoach general state and offers system actions :

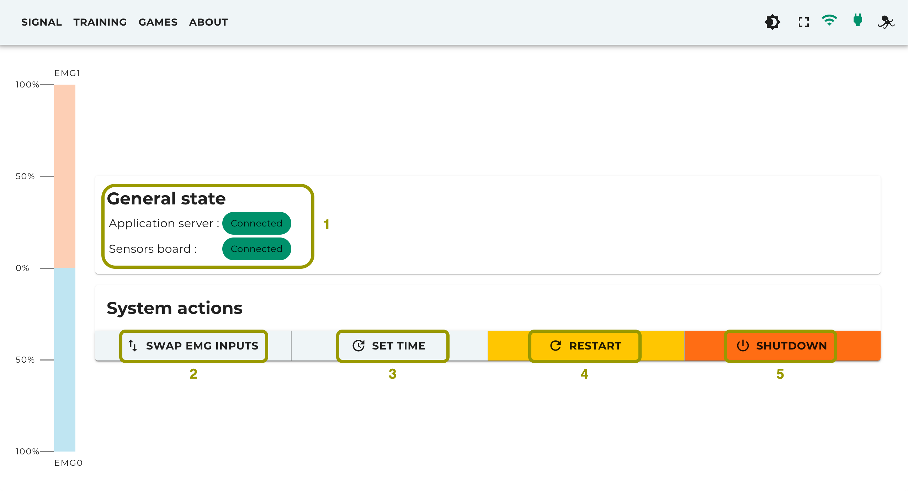
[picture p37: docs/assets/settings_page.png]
settings_page


* :one: - Shows if sensors cardboard and server are connected or not.
* :two: - Swap EMG inputs : When clicked, the EMG sensors inputs are swapped immediately. An alert notifies the users of the action effect.
* :three: - Set time : When clicked, it immediately sets the MyoCoach clock (Raspberry Pi internal clock) to the client device time. An alert notifies the users of the action effect.
* :four: - Restart : When clicked, a dialog view shows up to ask for confirmation to restart the system. An alert notifies the users of the action effect. If equipped, the LED button will blink in yellow until system effectively restarts.
* :five: - Shutdown : When clicked, a dialog view shows up to ask for confirmation to shut the system down. An alert notifies the users of the action effect. If equipped, the LED button will blink in red until system effectively shuts down.

## Wi-Fi Access Point administration

The MyoCoach includes an access point application setup called RaspAP to enable Wi-Fi connection to the MyoCoach web application. RaspAP allows the Raspberry Pi to work as a router and also has a web application for its administration.

### Getting started

* :one: - Make sure the MyoCoach web application "Getting started" section has been followed before to start this section.
* :two: - Connect your device to the MyoCoach Wi-Fi network.
* :three: - To access the AP administration web application, open a web browser window and go to the following address : http://raspap.myocoach.lan
* :four: - An authentication request dialog shows up :

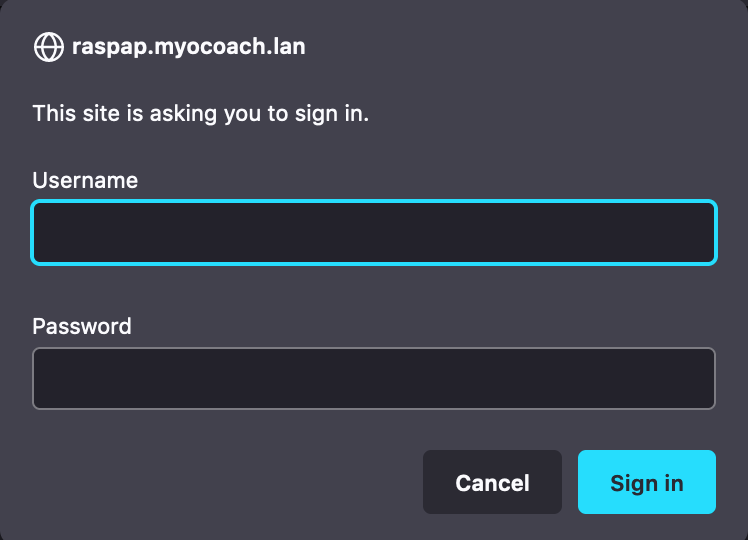
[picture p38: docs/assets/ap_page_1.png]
ap_page_1


The credentials can be :
   * previously configured following the [server-programming-manual](./server-programming-manual.md)).
   * not configured, default value - Username = admin, Password = secret

* :five: - Once the RaspAP web application access granted, the following page shows up where all configurations are available :

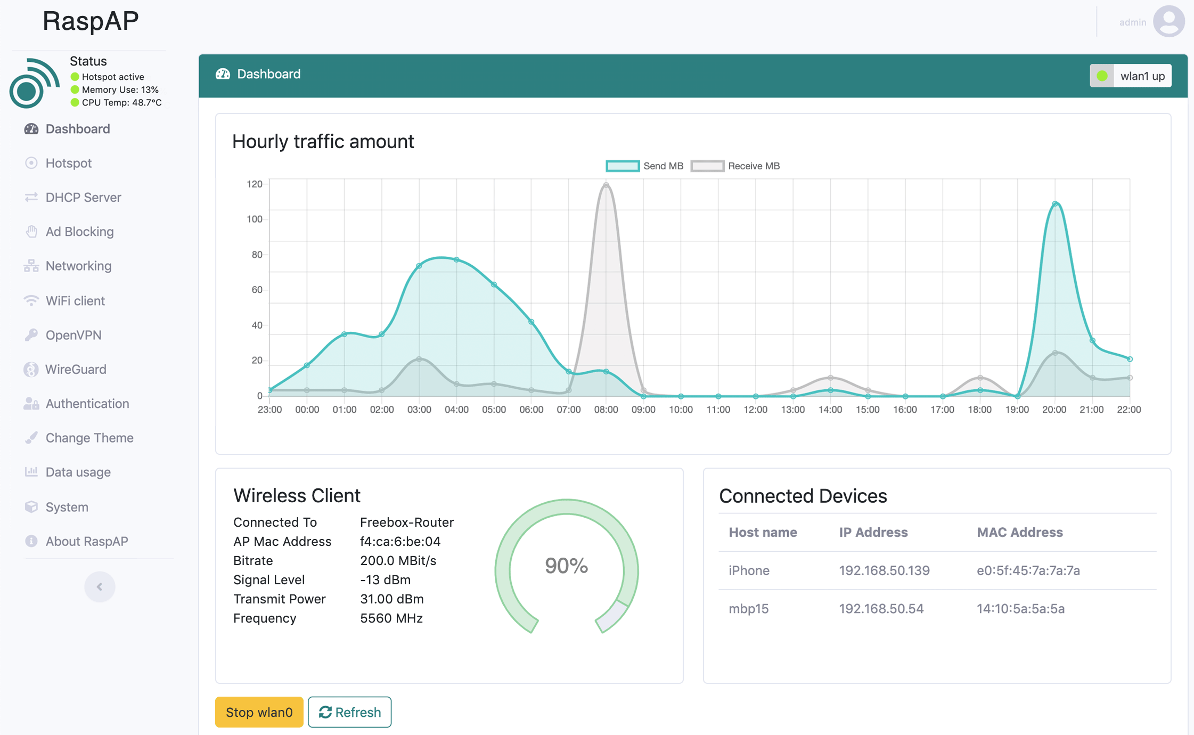
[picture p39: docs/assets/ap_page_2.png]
ap_page_2


* :six: - The complete RaspAP documentation is available at the following address : https://docs.raspap.com/

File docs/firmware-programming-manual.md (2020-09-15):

# 0113-MyoCoach-DIY :<br>Firmware Programming Manual

The Arduino board fulfils two roles:

* acquiring the signals from the EMG sensors on two analogue inputs
* sending this data to a computer via the USB port by emulating a serial link.

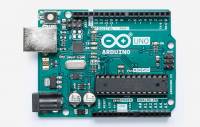
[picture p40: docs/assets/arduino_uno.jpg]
arduino_uno


The source code of the Arduino program is available in [src/software/firmware](../src/software/firmware)

At Orthopus, we use the online programming tool developed by Arduino. You can find help and information about this tool by following this link:
[Getting Started with Arduino Web Editor](https://create.arduino.cc/projecthub/Arduino_Genuino/getting-started-with-arduino-web-editor-on-various-platforms-4b3e4a?f=1)

## Programmation

* :one: Create an account on the online programming tool developed by Arduino: [Arduino Web Editor](https://create.arduino.cc)

* :two: Install the Arduino Web Editor [plugin](https://create.arduino.cc/getting-started/plugin)

> :bulb: At ORTHOPUS we use the Arduino Web Editor but it is also possible to use and install the Arduino IDE to program the board.

* :three: Importing the **myocoach.ino** file into the online code editor

* :four: Connecting the Arduino card to the computer
* :five: Transfer the MyoCoach programme to the Arduino card

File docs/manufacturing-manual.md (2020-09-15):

# 0113-MyoCoach-DIY : <br> Manufacturing Manual

In this manual you will find all the resources to design the various components of the MyoCoach.

* The [armband](#armband)
* The Arduino board [casing](#casing)

## List of equipment
To design the MyoCoach, you will need :

* A 3D printer
* PLA type filament
* An Arduino UNO type board [link](https://store.arduino.cc/arduino-uno-rev3)
* A female pin header strip [link](https://fr.farnell.com/samtec/ssq-110-03-f-s/connect-femelle-10-voies-1-rang/dp/2667433)
* A male pin header strip [link](https://fr.farnell.com/amp-te-connectivity/1-826629-0/barrette-droite-1-rangee-10voies/dp/3418376)
* A set of electronic cables [link](https://fr.farnell.com/pro-signal/psg-jws-65/jumper-wire-set-65pc/dp/2503764?MER=bn_level5_5NP_EngagementRecSingleItem_3)
* Self-tapping screws 8 x ∅2.2-L5 [link](https://www.visseriefixations.fr/catalog/product/view/id/38717)
* A strap with velcro and buckle [link](https://www.amazon.fr/gp/product/B07G9XFYM4/ref=ppx_yo_dt_b_asin_title_o05_s00?ie=UTF8&psc=1)

Tools :

* A Phillips screwdriver
* A soldering iron + soldering accessories
* A tube of glue type Glue

## The ArmBand
The armband is the component of the MyoCoach that holds the two Ottobock EMG sensors (Ref 13E202) on the residual limb of the future prosthesis user. This armband is comfortable, inexpensive and facilitates the positioning of the sensors for the ortho-prosthetist.

### Printing of the Sensor Supports
The supports have been made with Fusion360 software.

The file in .STL format is available in [src/hardware/casing](../src/hardware/casing)

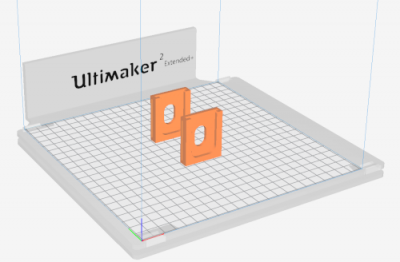
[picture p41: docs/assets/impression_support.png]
support print


### armband assembly
Prepare the different elements: the printed material, the strap and the EMG sensor.

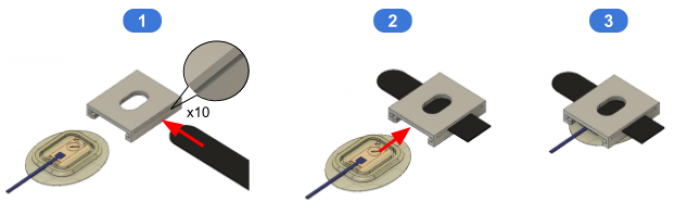
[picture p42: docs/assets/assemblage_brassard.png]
assemblage_brassard


* :one: Insert the strap into the side openings of the media.

> :bulb: The strap must be forced in.

* :two: Insert the Ottobock 13E202 sensor into the holder, taking care to force the strap between the holder and the sensor.

> :bulb: The sensor must go at the end of the mechanical stop in the holder.

### Adjustments and positioning
The design of the sensor holder and especially the design of the slot where the cable passes through offers a certain freedom of positioning between the two sensors. This freedom of movement allows the two EMG sensors to be correctly positioned above the user's muscle areas.

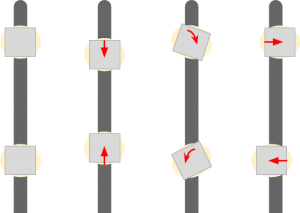
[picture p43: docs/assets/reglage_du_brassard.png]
reglage_du_brassard


## The Casing
The MyoCoach's case allows EMG sensor data to be acquired with an Arduino card and transferred to a computer for visualisation. It also allows the Ottobock electrode connector format to be adapted to the MyoCoach casing.

### Casing printing
The casing of the Arduino Board has been made with Fusion360 software.

STL format files are available in [src/hardware/casing](../src/hardware/casing)

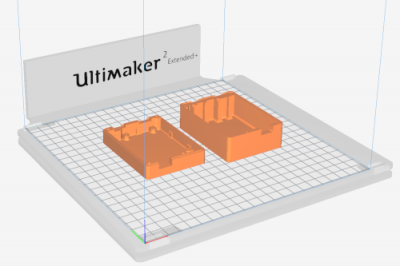
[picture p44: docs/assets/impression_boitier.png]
impression_boitier


### Preparation of the Arduino card
The main idea is to solder two female connectors (5-pin female pin header strips) to adapt to the female connectors of the Ottobock 13E202 sensors. The connectors are connected to the analogue ports A0 (EMG 0) and A1 (EMG 1) of the Arduino board.

The wiring diagram is as follows:

arduino layout

The result is as follows:

soudure connecteur

### Casing Assembly
Prepare the following items: the Arduino card, the two parts of the case, the female pin header strips and the 8 self-tapping screws.

assemblage_boitier_1

* :one: Insert the Arduino card into the case.

* :two: Screw in the 4 self-tapping screws to hold the Arduino card in the case.

assemblage_boitier_2

* :three: Using pliers, cut off the 2 outer pins of the snap-off strips.

* :four: To hold the connectors in place in the box, apply 2 drops of glue (Glue type) before placing the connectors in the box.

> :bulb: The cables are not shown in these illustrations but at this stage the connectors must be soldered.

assemblage_boitier_3

* :five: Close the housing

> :warning: Before closing the case, the connectors must be connected to the Arduino board (+5v, GND, EMG0 → A0, EMG1 → A1).

* :six: Turn the MyoCoach housing over and screw in the 4 self-tapping screws to hold the two housing covers in place.

### Electrode Connector
The connector of the Ottobock 13E202 electrodes is very specific.

connecteur_electrode

But a simple 3-pin header strip is used to interface between the electrodes and the connectors of the MyoCoach box.

adpatateur_electrode

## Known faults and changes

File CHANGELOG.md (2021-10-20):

# 0113-MyoCoach-DIY :<br>Changelog
All notable changes to this project will be documented in this file.

The format is based on [Keep a Changelog](https://keepachangelog.com/en/1.0.0/), and this project adheres to [Semantic Versioning](https://semver.org/spec/v2.0.0.html).

## [Unreleased]
* Add log system to store user information (sensor gain, game record, ...)

## [v2.0.0] - 2021-10-18
### Update
* Complete rewrite of the MyoCoach implementation using web technologies
* Installation based on a Raspberry Pi board with a Wi-Fi access point for an easier system setup
* Modern responsive web user interface
* Training exercises integration with custom trails management
* Framework for video games integration
* Convenient features such as fullscreen mode, night/day mode, EMG inputs swapping, system clock setting, system reboot or shutdown.
* Integration of a LED power button to the board that indicates system status (optional)
* Updated user-manual.md guide
* Updated arduino firmware file for an optimised EMG signal acquisition
* Monitoring of system components connectivity
### Added
* Added server-programming-manual.md guide

### Removed
* v.1.0 Graphical UI application code (src/software/ui/)
* Deleted ui-programming manual.md

## [v1.0.1] - 2020-09-24
### Fixed
* Add the CONTRIBUTING file about MyoCoach v2.0 ORTHOPUS ideas.

## [v1.0.0] - 2020-09-18
### Added
* The first full functional version of the MyoCoach with Arduino board and UI desktop application in Python

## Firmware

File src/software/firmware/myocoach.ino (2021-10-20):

void setup() {
  Serial.begin(9600); // Starts the serial communication
}
void loop() 
{
  
  int sensorValue1 = analogRead(A0);
  int sensorValue2 = analogRead(A1);
  
  // Convert the analog reading (which goes from 0 - 1023) to a voltage (0 - 5V):
  float e1 = map(sensorValue1,0,1023,0,255);
  float e2 = map(sensorValue2,0,1023,0,255);
  byte data = Serial.read();
  if(data == 's')
  {
    Serial.print(e1);
    Serial.print(":");
    Serial.print(e2); 
    Serial.println();
  }
  delay(10);
}

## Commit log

2020-09-03 Rename Folder with lower case
2020-09-10 Add manufacturing manual and part
    [Casing Down.stl, Casing Up.stl, Sensor Support 13E202.stl]
2021-10-18 Add: myocoach v2.0 source code and led-button management scripts
2021-10-20 Added missing setup instruction : captive portal, ledbutton
2021-10-20 Add raspberry gpio diagram for ledbutton wiring
2021-10-21 Fix ledbutton setup procedure mistakes
2021-10-21 Fix ledbutton scripts path mistakes
